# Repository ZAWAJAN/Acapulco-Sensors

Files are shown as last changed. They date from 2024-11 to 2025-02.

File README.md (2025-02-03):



# Acapulco Light Sensors: The Cube and The Camera

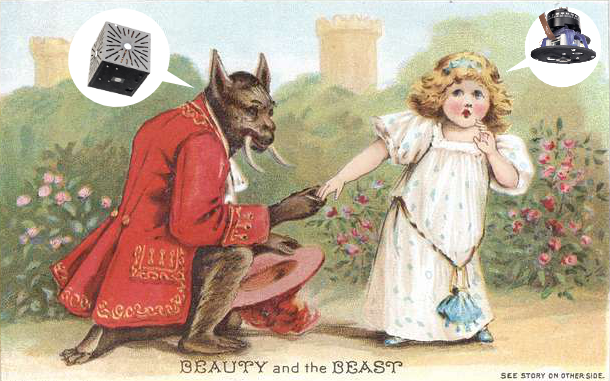
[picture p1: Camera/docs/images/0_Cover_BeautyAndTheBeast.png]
Project Cover - The Beauty and The Beast


## Introduction

The Cube (cubic illuminance sensor) and the Camera (HDR image generation setup) sensors were developed as open hardware devices to support predictive building control as part of the [Acapulco](https://www.thegreenvillage.org/project/acapulco/) research project at the [TU Delft Green village](https://www.thegreenvillage.org/).
The Acapulco project, based in the TU Delft Green Village, The Netherlands, is developing innovative design tools to optimise the sustainability of heating, cooling and lighting systems in commercial buildings. The project focuses on integrating thermal storage, a heat pump with ground and surface water sources, automated outdoor Venetian blinds, daylight-linked lighting controls, and AI-powered predictive controls to enhance energy efficiency, reduce CO2 emissions, and alleviate grid congestion.

## Sensing Devices

The project uses two environmental sensing devices, which are referred to as "sensors" in this documentation. 
Each device is in fact a collection of various sensors and parts.
The two devices are used in combination in the Acapulco project, however, one can be used without the other as they are completely independent in their functions.

In two separate folders you can find all needed instructions to assemble and use the two sensors:
1. [**The Cube**](Cube/)
	- A cubic open-source illuminance sensor designed for environmental monitoring (The Cube).
	- The Cube uses a Raspberry Pi Zero 2W with "Ambient 2 Click" sensors connected via a multiplexer, with additional temperature and humidity sensors, all enclosed in a laser-cut box.
 	- Concept inspired by the work of Xia, L., Pont, S. C., & Heynderickx, I. (2017). *Light diffuseness metric, Part 2: Describing, measuring and visualising the light flow and diffuseness in three-dimensional spaces.* Lighting Research & Technology, 49(4), 428–445. [https://doi.org/10.1177/1477153516631392](https://journals.sagepub.com/doi/10.1177/1477153516631392)
2. [**The Camera**](Camera/)
	 - A camera setup for HDR image generation (The Camera).
	 - The Camera uses a Raspberry Pi 4B, with one additional "Ambient 2 Click" sensor for luminance validation. Attached to the ceiling by 3D-printed parts and standard camera mounting elements.
 	 - Concept inspired by the work of Kruisselbrink, T., Aries, M., & Rosemann, A. (2017). A Practical Device for Measuring the Luminance Distribution. International Journal of Sustainable Lighting, 19(1), 75–90. [https://doi.org/10.26607/ijsl.v19i1.76](https://lightingjournal.org/index.php/path/article/view/76)

## Authors

The sensors design, production, and calibration were performed by:
- [Jan Zawadzki](https://www.linkedin.com/in/jan-zawadzki-a92650213/)
- [Eleonora Brembilla](https://www.tudelft.nl/en/staff/e.brembilla/)
- [Pedro de la Barra Luegmayer](https://www.tudelft.nl/en/staff/p.delabarraluegmayer/)
- [Wouter Beck](https://www.linkedin.com/in/wouterbeck/)

## Acknowledgments 

The development of these sensors was supported by a [Open Hardware Stimulation Fund](https://www.tudelft.nl/open-hardware) from the [TU Delft Open Science Program](https://www.tudelft.nl/en/open-science) and by the RVO MMIP Acapulco project (Grant number TSEGO23017).

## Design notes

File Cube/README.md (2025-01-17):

# Cubic Illuminance Sensor

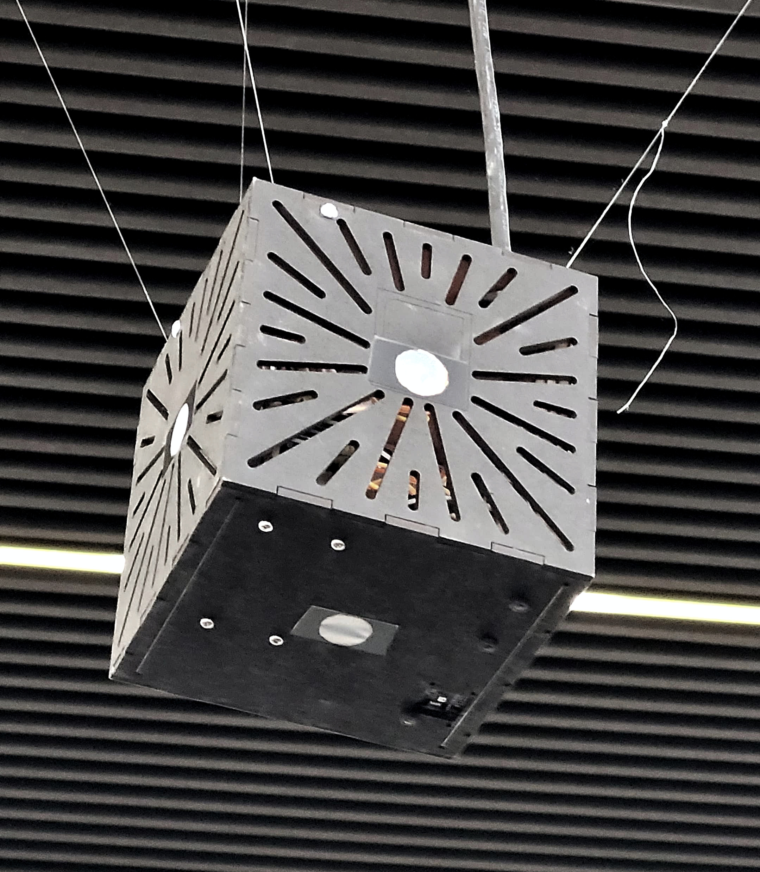
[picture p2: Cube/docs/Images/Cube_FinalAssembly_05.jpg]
Final Cube Image


An open-source cubic illuminance meter designed for environmental monitoring. The device uses a Raspberry Pi Zero with "Ambient 2 Click" sensors connected via a multiplexer, all enclosed in a laser-cut box.

## Features
- Measures ambient light in multiple directions (cubic configuration).
- Customizable design using off-the-shelf components.
- Built with open-source hardware and software principles.

## Table of Contents
1. [Introduction](#introduction)
2. [Bill of Materials (BOM)](#bill-of-materials-bom)
3. [Calibration Setup](#calibration-setup)
4. [Final Setup](#final-setup)
5. [Usage Instructions](#usage-instructions)
6. [Troubleshooting](#troubleshooting)
7. [Contributing](#contributing)
8. [License](#license)

## Introduction
The Cubic Illuminance Sensor is designed to measure light levels from different angles for environmental sensing applications. It is based on a Raspberry Pi Zero 2W and 6 "Ambient 2 Click" sensors.

It is assumed that building such a sensor requires previous knowledge and intent on its purpose. 

If you want to learn more, please refer to [the paper](https://journals.sagepub.com/doi/full/10.1177/1477153516631392) on which our design is based on.

## Bill of Materials (BOM)

The bill of materials can also be found in an excel file [Materials_Bill](Materials_Bill.xlsx). Depending on your location there might be different available providers and prices, but we included the ones we used as a reference.

| Component               | Quantity | Description                           | Example Link                       |
|-------------------------|----------|---------------------------------------|----------------------------|
| Raspberry Pi Zero 2W       | 1        | Small form-factor computer            | [Buy here](https://www.raspberrypi.com/products/raspberry-pi-zero-2-w/)               |
| Raspberry Pi Zero 2W PoE HAT | 1 | Add-on to Raspberry Pi enabling power and data input with just one ethernet cable | [Buy here](https://www.kiwi-electronics.com/en/poe-ethernet-usb-hub-hat-for-rpi-zero-10711)
| Raspberry Pi Zero 2W Heatsink | 1 | Add-on for Raspberry Pi to better dissipate heat generated by the chips | [Buy here](https://www.waveshare.com/zero-heatsink.htm) |
| Ambient 2 Click         | 6        | MikroElektronika Ambient 2 Click Light Sensor mikroBus Click Board | [Buy here](https://nl.rs-online.com/web/p/sensor-development-tools/1360740)               |
| Temperature & Humidity Sensor | 1 | Adafruit AHT20 - Temperature & Humidity Sensor Breakout Board | [Buy here](https://www.kiwi-electronics.com/nl/adafruit-aht20-temperature-humidity-sensor-breakout-board-stemma-qt-qwiic-10419) |
| I2C Multiplexer    | 1        | IC TCA9548A I2C Multiplexer - Adafruit 2717 breakout board for sensor connection | [Buy here](https://www.bitsandparts.nl/IC-TCA9548A-I2C-Multiplexer-Adafruit-2717-breakout-board-p113670)  |
| Ethernet cable | 1 | Ethernet cable for connection, length as needed | [Buy here](https://www.allekabels.nl/utp-kabel/7390/1098220/uutp-kabel-cat-5e.html) |
| Laser-cut MDF case  | 1        | The laser cut elements for custom enclosure assembly. 3mm MDF or other hard sturdy material.   | [CAD Files](#)              |
| Miscellaneous hardware  | -        | Screws, spacers, wiring, etc.         | -                           |

## 1. Calibration Setup

First, you have to calibrate the ==Ambient2Click== sensors. Refer to the [Sensors Calibration Guide](docs/01_Calibration.md) for instructions on how to do it.

## 2. Final Cube Assembly and Setup

After the sensors are calibrated, you can proceed to assemble the final cubic enclosure for all components.

Refer to the [Final Production Guide](docs/02_Final_Production_And_Assembly.md) for instructions.

## 3. Software

Software instructions can be found in the [Running Software](docs/03_Running_Software.md) guide.

## Troubleshooting
- [Common Issues and Solutions](docs/04_Cube_TroubleShooting.md)

## License
This project is licensed under the [MIT License](LICENSE).

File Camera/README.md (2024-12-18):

# Camera HDR sensor

This repository enables you to use commonly available modular components to build an HDR image capture device, 
compliant with Radiance software suite. It comprises of hardware and software to go through calibration process and
mount the camera on the ceiling, or anywhere else, like in the field.

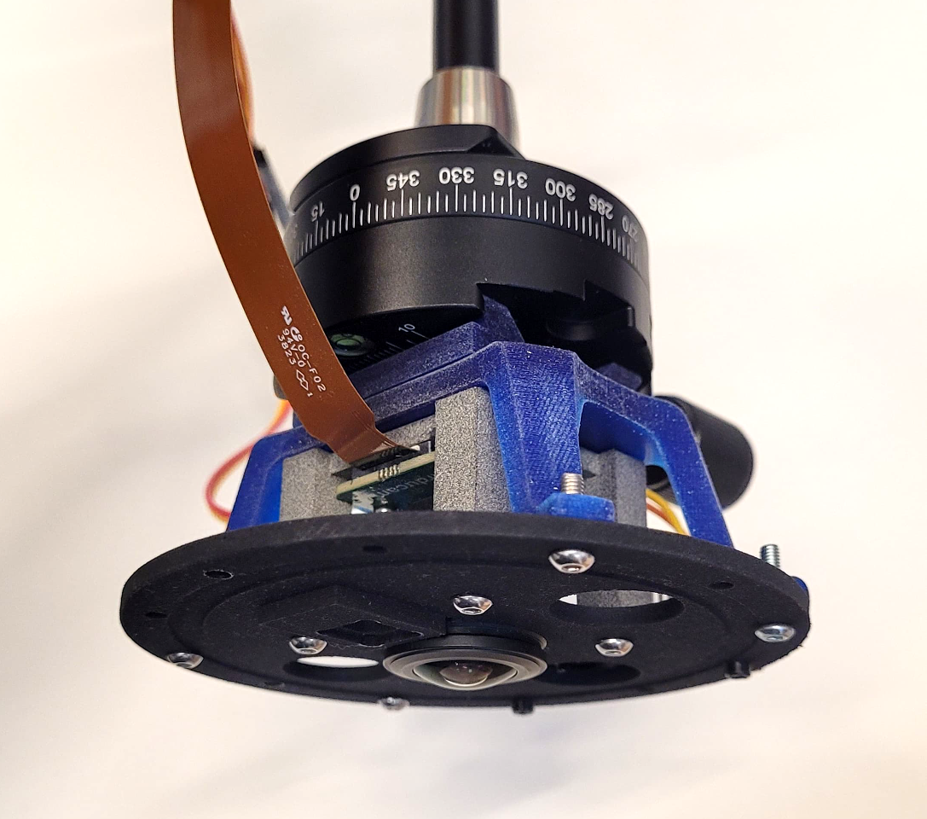
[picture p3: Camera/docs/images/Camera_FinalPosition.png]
Camera attached to the main mounting hold and a regulated arm


## Features
- A low cost way to produce an HDR image remotely, periodically, or in awkward places...
- Takes a series of pictures with varying exposures
- Creates an HDR image using [hdrgen](http://www.anyhere.com/) software
- Via [Radiance](https://www.radiance-online.org/) software, it applies corrections defined during calibration 
process to end up with a proper final HDR image
- Additionally measures luminosity value with an Ambient2Click sensor, for later validation.

## Table of Contents
1. [Introduction](#introduction)
2. [Bill of Materials (BOM)](#bill-of-materials-bom)
3. [Hardware Setup](#hardware-setup)
4. [Software Setup](#software-setup)
5. [HDR Camera Calibration](#hdr-camera-calibration)
6. [Usage Instructions](#usage-instructions)
7. [Troubleshooting](#troubleshooting)
8. [License](#license)

## Introduction

The device uses a Raspberry Pi 4B with an Arducam fisheye camera in order to produce an HDR image. Additionally, 
an illuminance sensor is attached to record a reading that can be helpful later to validate HDR image. The produced 
HDR image can be later used in light studies, glare analysis etc.

## Bill of Materials (BOM)
| Component                  | Quantity | Description                                                                               | Link                       |
|----------------------------|----------|-------------------------------------------------------------------------------------------|----------------------------|
| Raspberry Pi 4B (or other) | 1        | Small form-factor computer. The design also works with other models.                      | [Example](https://www.raspberrypi.com/products/raspberry-pi-4-model-b/)               |
| Raspberry Pi 4 PoE HAT     | 1        | Add-on to Raspberry Pi enabling power and data input with just one ethernet cable         | [Example](https://www.raspberrypi.com/products/poe-plus-hat/)               |
| Raspberry Pi Camera        | 1        | 180° fisheye camera for Raspberry Pi, Arducam Mini imx477 with 180° LN031 fisheye lens    | [Example](https://www.arducam.com/product/arducam-12mp-imx477-mini-high-quality-camera-module-for-raspberry-pi/) |
| Ambient 2 Click sensor     | 1        | MikroElektronika Ambient 2 Click Light Sensor mikroBus Click Board                        | [Example](https://nl.rs-online.com/web/p/sensor-development-tools/1360740)            |
| Ethernet cable             | 1        | Ethernet cable for connection, lenght as needed                                           | [Example](https://www.allekabels.nl/utp-kabel/7390/1098220/uutp-kabel-cat-5e.html)    |
| 3D printed parts           | 1        | High quality, preferably stereolithography polyjet, resin or similar, pla will not cut it  | [CAD Files](src/hardware) |
| Quick Release Rotating Head| 1        | Standard Camera equipment quick release rotating head, preferably with a level meter      | [Example](https://www.kamera-express.nl/b-i-g-qr-60p-panorama-snelkoppeling-60mm)     |
| Laser-cut MDF parts        | 1        | Optional laser cut elements. 3mm MDF or other hard sturdy material.                       | [CAD Files](src/hardware) |
| Miscellaneous hardware     |          | M3 Screws, bolts, and nuts; wires, Rpi camera cable, etc.                                 | Depends on your location  |

## Hardware Setup

0. **3D Printing of parts:**
	- To save time and money, you can produce all the parts at once. You have to do it first anyway.
	- Before doing that, please go through the whole documentation first to know what is needed for what. And if you need to do any adjustments in the CAD files.
	- With the camera ring hold and the lux sensor bracket you have an option, it can be either 3D-printed or laser cut.
	- Parts should be 3D printed in a high quality and sturdy technology, like stereolitography polyjet or resin.
	- You will find all the files in the [hardware folder](src/hardware)
1. **Main Camera Hold:**
	- Camera is being held by a base circular piece in all circumstances.
	- You can refer to the [Main Camera Hold Assembly Guide](docs/00_Camera_Hold_Assembly.md).
1. **Calibration Stand Setup:**
	- You may start with calibrating the camera first, thus better start with assembling the calibration stand.
	- Follow the [Calibration stand assembly guide](docs/01_Camera_Calibration_Assembly.md).
2. **Final Camera Mount:**
	- After the camera is calibrated and all of the correction parameters are defined, you are ready to put your device 
	in place.
	- The final mounting place highly depends on your circumstances, but the use of commonly available camera equipment 
	makes it easy to adjust.
	- Follow the [Final mount assembly guide](docs/02_Camera_Final_Assembly.md).
3. **Wiring Diagram:**
	- In all steps, the wiring stays the same. Refer to the [Wiring Diagram](docs/images/Camera_Wiring_Diagram.png)
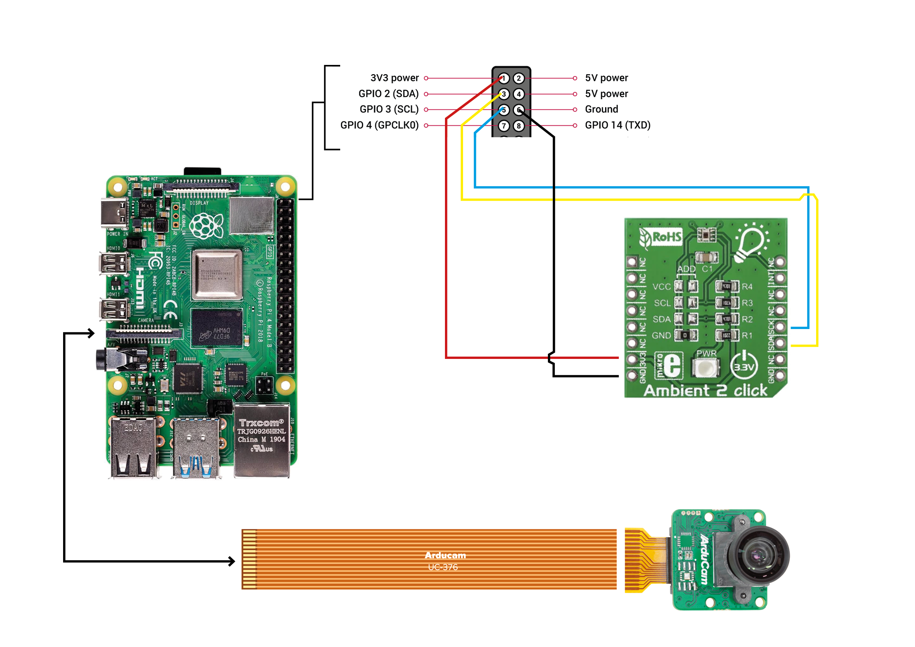
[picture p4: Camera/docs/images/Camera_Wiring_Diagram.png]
Wiring Diagram
	- 

## Software Setup

Before anything, you also have to set up the software needed for everything to run properly.

The software stack that we use is based on the [piHDR](https://github.com/andyrew/piHDR) repository and scripts.

Basic software like [picamera2](https://pypi.org/project/picamera2/) library should be installed automatically 
on your Raspberry Pi, but other things like [Radiance](https://www.radiance-online.org/) is quite tricky to install 
on a Raspberry Pi and looks like rarely anyone is actually doing it. 
But we do!

1. **Installation - Dependencies:**
	- Python - comes by default on the Raspberry Pi Bookworm OS
	- [picamera2](https://github.com/raspberrypi/picamera2) library - should also come by default.
	- [hdrgen](http://www.anyhere.com/) - download the image builder for Raspberry Pi. Or alternatively run:
	 ```bash
	 wget http://www.anyhere.com/gward/pickup/hdrgen_AMDRaspian.tar.gz
	 tar -xf hdrgen_AMDRaspian.tar.gz
	 sudo mv hdrgen /usr/local/bin/.
	 sudo mv hdrcvt /usr/local/bin/.
	 ```
	- imagemagick:
	 ```bash
	 sudo apt-get install imagemagick
	 ```
2. **Enable the Camera Module:**
	- Make sure your camera is connected and works properly.
	- Check the [camera dcumentation](https://www.raspberrypi.com/documentation/computers/camera_software.html)
	- Or alternatively the simple [starters guide](https://projects.raspberrypi.org/en/projects/getting-started-with-picamera/0)
3. **Install and Compile Radiance:**
	- Compiling Radiance on Raspberry Pi can be challenging, especially on newer OS like Bookworm.
	- Refer to the [Radiance Compile Guide](docs/03_Camera_Software_Radiance_Compile.md) to get instructions on 
	how to do it properly, so every app will work.
4. **First run:**
	- Go to the [Usage Instructions](#usage-instructions) and check if things work.
	- Before [Camera Calibration](#hdr-camera-calibration) process, you can only make a basic HDR image, as you don't 
	have the necessary parameters for Radiance correction executables.
## HDR Camera calibration

Each camera module and fisheye lens is different, even if they come from the same manufacturer and the same line.

That's why it's important to apply corrections to the HDR image taken based on those discrepancies. Those corrections 
	are applied with various Radiance apps in the main [bash script](src/code/run_hdrcapture.sh) in consecutive lines after creating 
	an HDR image.

See the [Calibration Guide](docs/04_Camera_Calibration_Guide.md) for detailed instructions.

## Usage Instructions

- In order to only take multiple exposures (images), you can use the python script `exposurebracket.py`.
	 ```bash
	 python3 exposurebracket.py
	 ```
- To run the whole software, simply run `run_hdrcapture.sh`, which will call all necessary scripts and apps.
	 ```bash
	 bash run_hdrcapture.sh
	 ```
- The script will create a new folder in which everything will be stored.
- It also calls the `lux_sensor.py` script providing it with the timestamp. This stores the lux value from the sensor.
- **Note!** In consecutive lines of the `run_hdrcapture.sh`, after the `hdrgen` is run, you can apply various corrections to 
	the HDR via `ra_xyze, pcompos, pfilt` and `pcomb`. Those require parameters and correction `.cal` files specific 
	to your situation, which have to be defined through the calibration process. 
	Again refer to [HDR Camera Calibration](#hdr-camera-calibration)

## License
This project is licensed under the [Solderpad License](http://solderpad.org/licenses/SHL-2.1/).

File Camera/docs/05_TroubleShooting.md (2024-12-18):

# Troubleshooting

## Common Issues
1. **No Sensor Data**
   - Check that the multiplexer is connected properly.
   - Verify that the sensors are powered.

2. **Incorrect Data Readings**
   - Make sure the sensors are not obstructed.
   - Check for proper sensor calibration in the software.

3. **Software Installation Fails**
   - Try running the software with elevated privileges (`sudo`).

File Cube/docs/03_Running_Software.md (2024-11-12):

# Software Guide for Cube Illuminance meter

Now that you have the assembled device ready, you can collect the data from it. There are numerous ways, the data can be collected once, when needed, or it could be a chronological setup, for example using 'cron'.
The code to be used is pretty much the same as the one used during calibration.

Remember to apply the adjustments figured out during the calibration process. That needs to be done by hardcoding it into the provided [python script](src/code/sensor_data_collect_store_csv.py).

# Usage Instructions

You can run the python script directly from the command line, providing a name of the csv file to store the data in, like so:
```bash
python3 sensor_data_collect_store_csv.py "Data_Log_File.csv"
```

Or you could use the [bash script](src/code/run_sensor_collector.sh), which automatically creates a folder named with this days timestamp. In the bash script, at the beginning you can specify the desired directory.
```bash
bash run_sensor_collector.sh
```

The sensor is meant to collect data periodically. 
To set this up, we refer you to [this example guide on cron](https://phoenixnap.com/kb/set-up-cron-job-linux).

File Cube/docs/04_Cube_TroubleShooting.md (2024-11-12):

# Troubleshooting

## Common Issues
1. **No Sensor Data**
	- Check that everything is connected properly.

2. **Incorrect Data Readings**
	- Make sure the sensors are not obstructed.
	- Did you calibrate the sensor properly?

3. **Software Installation Fails**
	- Try running the software with elevated privileges (`sudo`).

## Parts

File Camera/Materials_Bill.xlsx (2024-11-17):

Component | Quantity | Description | Sample Link
Raspberry Pi 4B (or other) | 1 | Small form-factor computer. The design also works with other models. | https://www.raspberrypi.com/products/raspberry-pi-4-model-b/
Raspberry Pi 4 PoE HAT | 1 | Add-on to Raspberry Pi enabling power and data input with just one ethernet cable | https://www.raspberrypi.com/products/poe-plus-hat/
Raspberry Pi Camera | 1 | 180° fisheye camera for Raspberry Pi, Arducam Mini imx477 with 180° LN031 fisheye lens | https://www.arducam.com/product/arducam-mini-high-quality-camera-with-m12-mount-lens-for-raspberry-pi-cm-cm3-cm3-cm4-b0271/
Ambient 2 Click sensor | 1 | MikroElektronika Ambient 2 Click Light Sensor mikroBus Click Board | https://nl.rs-online.com/web/p/sensor-development-tools/1360740
Ethernet cable | 1 | Ethernet cable for connection, lenght as needed | https://www.allekabels.nl/utp-kabel/7390/1098220/uutp-kabel-cat-5e.html
3D printed parts | 1 | High quality, preferably stereolitography polyjet, resin or similar, pla will not cut it | depends on your local availability
Laser-cut MDF parts | 1 | Optional laser cut elements. 3mm MDF or other hard sturdy material. | depends on your local availability
Miscellaneous hardware |  | Screws, bolts, nuts, wiring, Rpi camera cable, etc.

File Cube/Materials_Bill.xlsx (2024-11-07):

Component | Quantity | Description | Sample Link
Raspberry Pi Zero 2W | 1 | Small form-factor computer | https://www.raspberrypi.com/products/raspberry-pi-zero-2-w/
Raspberry Pi Zero 2W PoE HAT | 1 | Add-on to Raspberry Pi enabling power and data input with just one ethernet cable | https://www.kiwi-electronics.com/en/poe-ethernet-usb-hub-hat-for-rpi-zero-10711
Raspberry Pi Zero 2W Heatsink | 1 | Add-on for Raspberry Pi to better dissipate heat generated by the chips | https://www.waveshare.com/zero-heatsink.htm
Ambient 2 Click sensors | 6 | MikroElektronika Ambient 2 Click Light Sensor mikroBus Click Board | https://nl.rs-online.com/web/p/sensor-development-tools/1360740
Temperature & Humidity Sensor | 1 | Adafruit AHT20 - Temperature & Humidity Sensor Breakout Board | https://www.bitsandparts.nl/IC-TCA9548A-I2C-Multiplexer-Adafruit-2717-breakout-board-p113670
I2C Multiplexer | 1 | IC TCA9548A I2C Multiplexer - Adafruit 2717 breakout board | https://www.kiwi-electronics.com/nl/adafruit-aht20-temperature-humidity-sensor-breakout-board-stemma-qt-qwiic-10419
Ethernet cable | 1 | Ethernet cable for connection, lenght as needed | https://www.allekabels.nl/utp-kabel/7390/1098220/uutp-kabel-cat-5e.html
Laser-cut MDF case | 1 | The laser cut elements for cube box assembly. 3mm MDF or other hard sturdy material.
Miscellaneous hardware |  | Screws, spacers, wiring, etc.

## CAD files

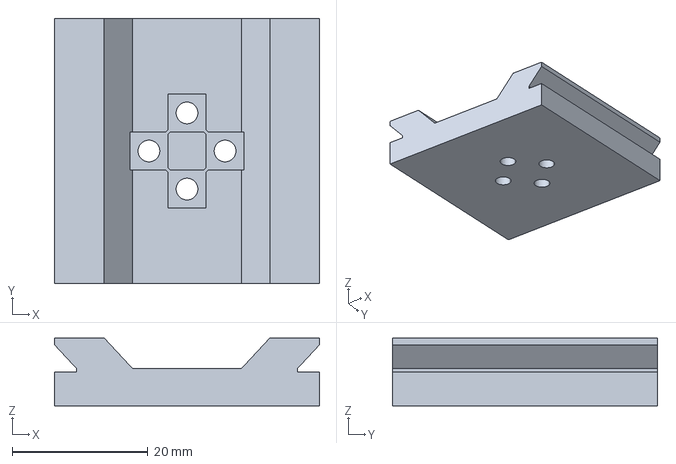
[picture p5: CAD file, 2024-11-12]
Camera/src/hardware/Camera_Mount_Slider.stp
39.0 x 39.0 x 10.0 mm

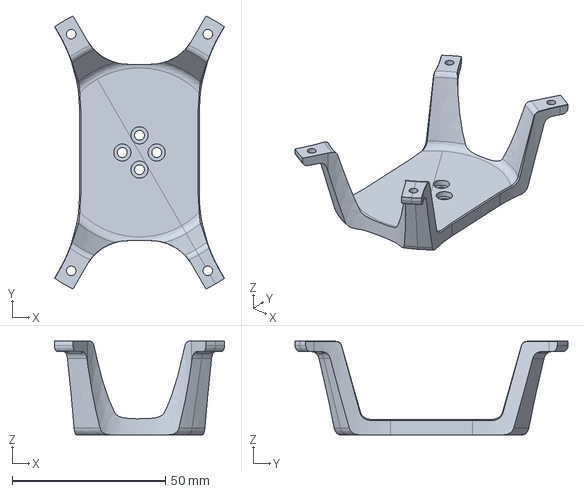
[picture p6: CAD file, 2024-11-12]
Camera/src/hardware/Camera_Mount_Claw.stp
55.4 x 89.0 x 30.5 mm

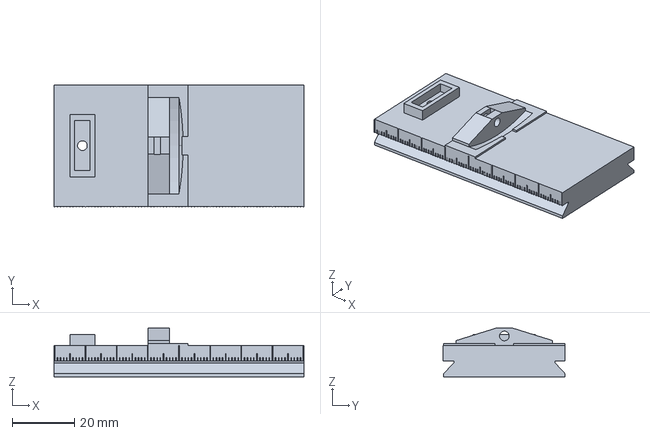
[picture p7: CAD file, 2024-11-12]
Camera/src/hardware/Camera_Calibration_Slider.stp
80.3 x 39.3 x 15.6 mm

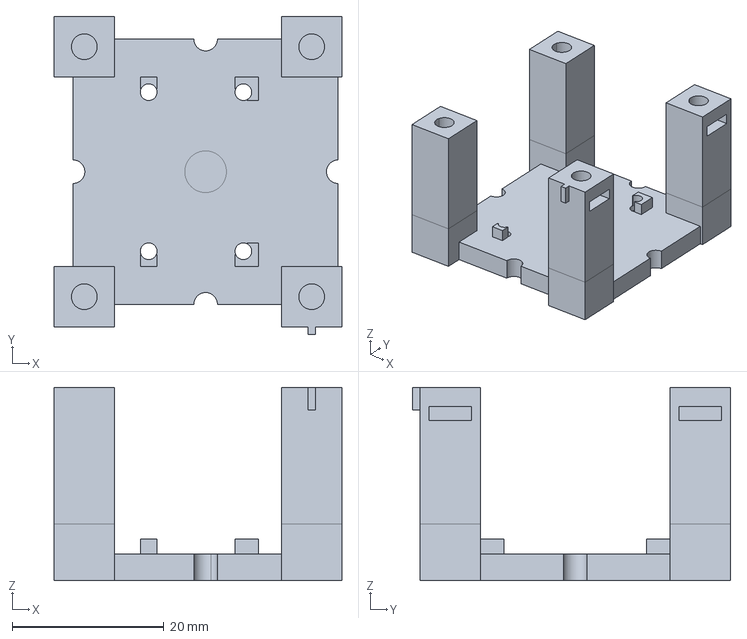
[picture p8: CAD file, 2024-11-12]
Camera/src/hardware/Camera_RingSpacer.stp
38.0 x 42.0 x 25.5 mm

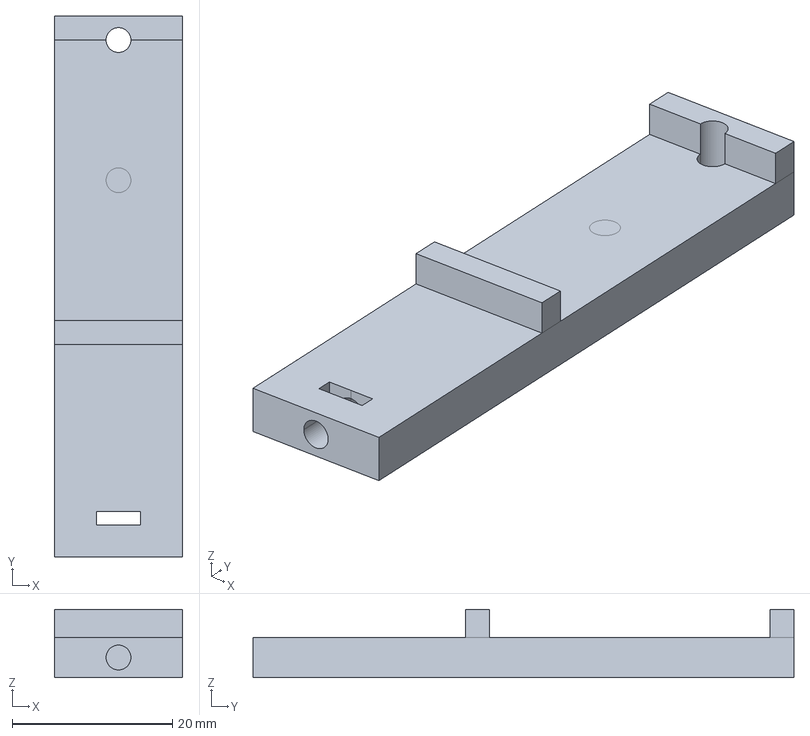
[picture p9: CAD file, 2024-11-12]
Camera/src/hardware/Camera_Calibration_VerticalStand.stp
16.0 x 67.5 x 8.50 mm

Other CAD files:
Camera/src/hardware/Camera_Ring.stp
Cube/src/hardware/Calibration_Bench.dwg
Cube/src/hardware/Cube_Box_Enclosure.dwg
Camera/src/hardware/Camera_RingAndSensorBracket.dwg
Camera/src/hardware/Camera_Calibration_Slider.stl
Camera/src/hardware/Camera_Calibration_VerticalStand.stl
Camera/src/hardware/Camera_Mount_Claw.stl
Camera/src/hardware/Camera_Mount_Slider.stl
Camera/src/hardware/Camera_Ring.stl
Camera/src/hardware/Camera_RingSpacer.stl

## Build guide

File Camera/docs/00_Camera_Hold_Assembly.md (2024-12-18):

# Camera Hold Assembly Guide

In this quick guide you will see instructions on how to assemble the main circular piece that holds the camera. 
That is used further in calibration and final positioning.

**You will need M3 bolts (9-12mm) and M3 square (5.5x5.5mm) nuts for assembly.**

## Assembly Steps

1. **Produce the pieces:**
	- First you need to produce the pieces:
		- Ring - can be 3D printed or laser cut
		- Spacer - Need to be 3D printed
		- Sensor bracket - can be laser cut or 3D printed
	- The Spacer can be 3D printed using [Camera_RingSpacer](../src/hardware/Camera_RingSpacer.stl) file. [STEP](../src/hardware/Camera_RingSpacer.stp) version is also available.
	- The Ring can be 3D printed using [Camera_Ring](../src/hardware/Camera_Ring.stl) file. [STEP](../src/hardware/Camera_Ring.stp) version is also available.
	- The **Ring** can also be laser cut together with the **Sensor Bracket** using the [Camera_RingAndSensorBracket](../src/hardware/Camera_RingAndSensorBracket.dwg) file.
2. **Screw the Camera plate to the Ring Spacer:**
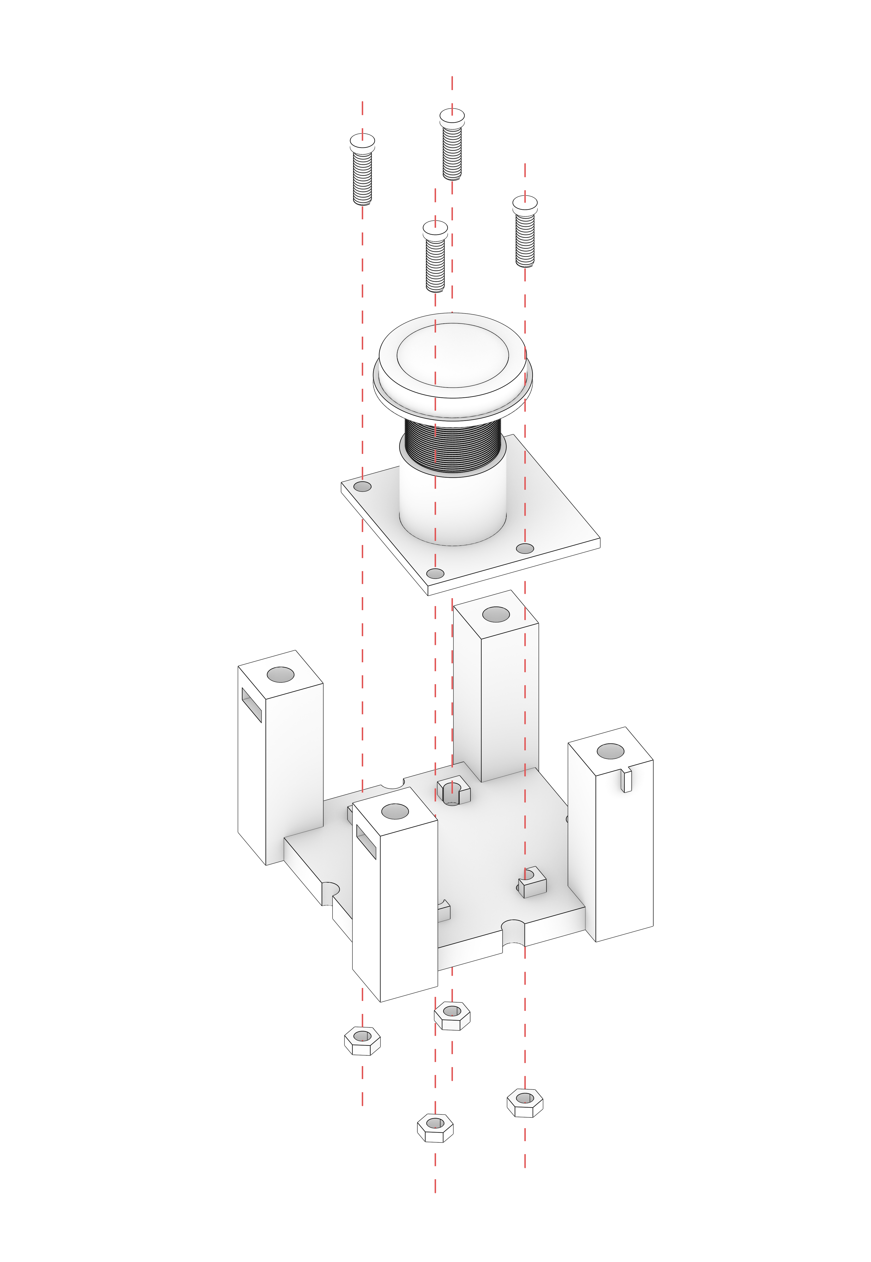
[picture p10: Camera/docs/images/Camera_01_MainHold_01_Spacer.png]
Screw the camera to the spacer
	- 
	- Make sure the camera pcp plate is being screwed in the right position, so that it will be centered with the circular piece and the camera hole.
3. **Screw the Spacer to the Ring:**
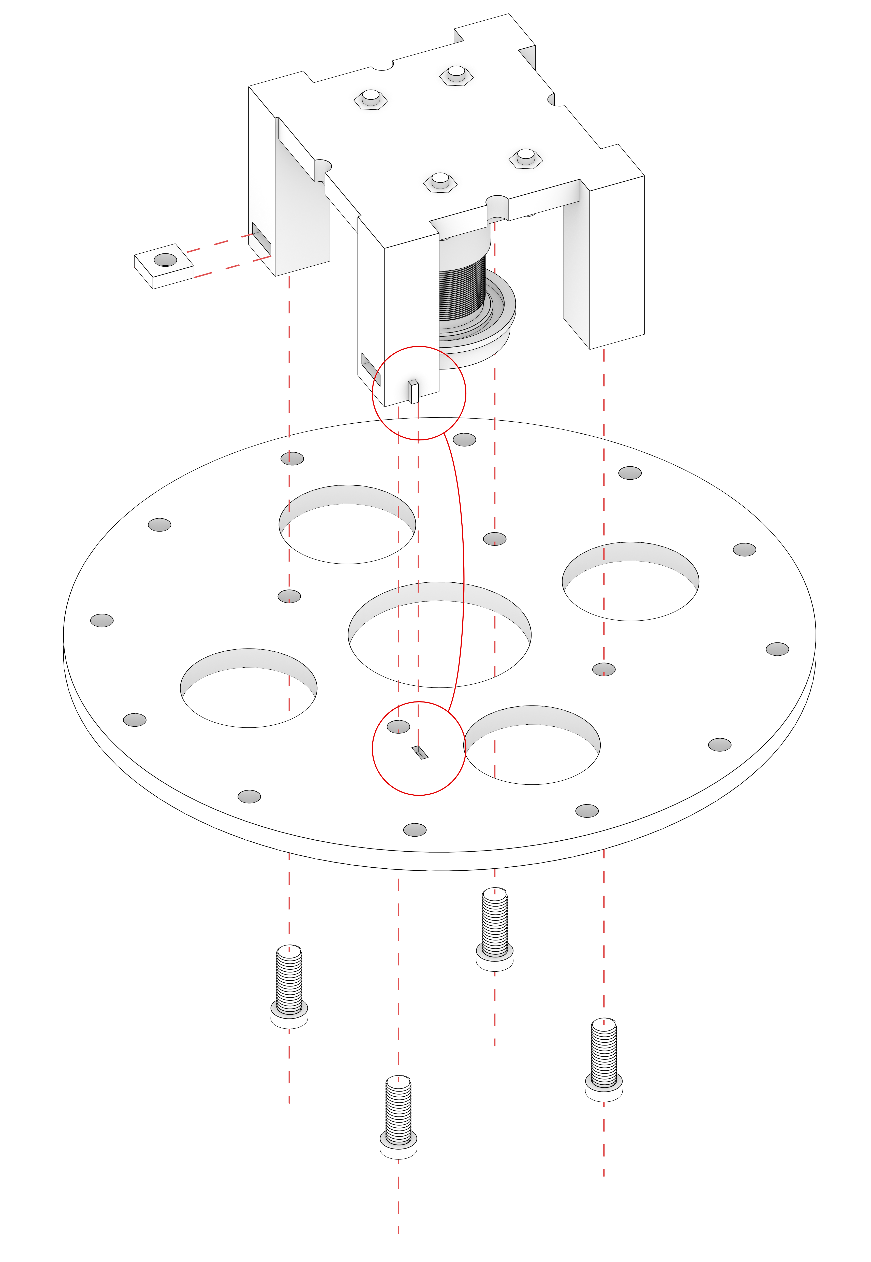
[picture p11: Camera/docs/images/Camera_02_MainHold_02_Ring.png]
Screw the Spacer with Camera to the Ring
	- 
	- Note the small notch on one of the Spacer legs, it tells you how to position it relative to the Ring. This notch should match the small mark on the Ring.
	- Put the square nuts in the special cavities in the Spacer legs.

## End Result

It should look like this after the assembly:

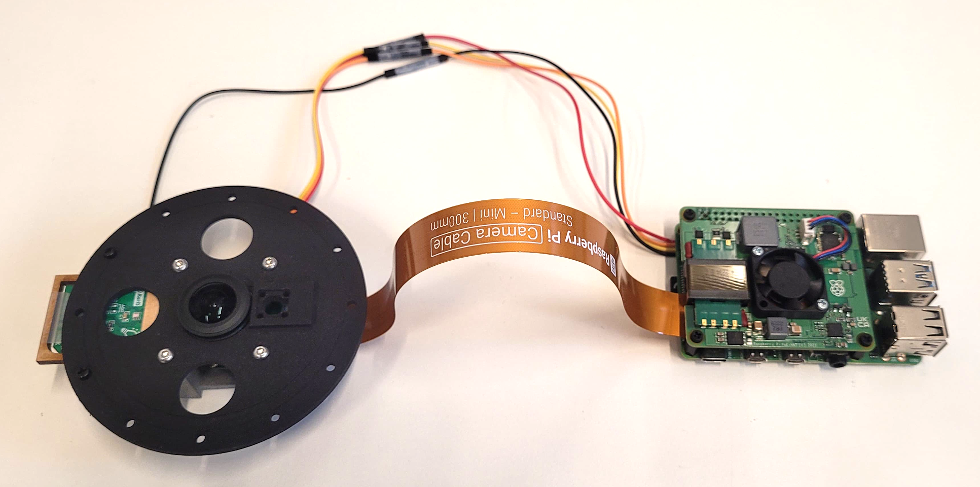
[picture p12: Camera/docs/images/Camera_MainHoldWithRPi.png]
Main Camera Hold Assembled and connected to Raspberry Pi


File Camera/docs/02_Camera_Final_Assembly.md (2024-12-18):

# Camera calibration Stand Assembly Guide

Here you will find instructions on how to assemble the final mounting equipment for the Camera.
You can then use it as you wish depending on where you want the camera to be positioned.

**You will need M3 bolts (9-12mm) and M3 square (5.5x5.5mm) nuts for assembly.**

## Assembly Steps

1. **Produce the pieces:**
	- Here you will need the _Claw_ that holds the Camera ring and the _Slider_ which can be mounted on the Quick Release Head.
	- Both parts need to be 3D printed on high quality:
		- [Camera_Mount_Claw](../src/hardware/Camera_Mount_Claw.stl). - [STEP version](../src/hardware/Camera_Mount_Claw.stp).
		- [Camera_Mount_Slider](../src/hardware/Camera_Mount_Slider.stl). - [STEP version](../src/hardware/Camera_Mount_Slider.stp).
2. **Assemble parts:**
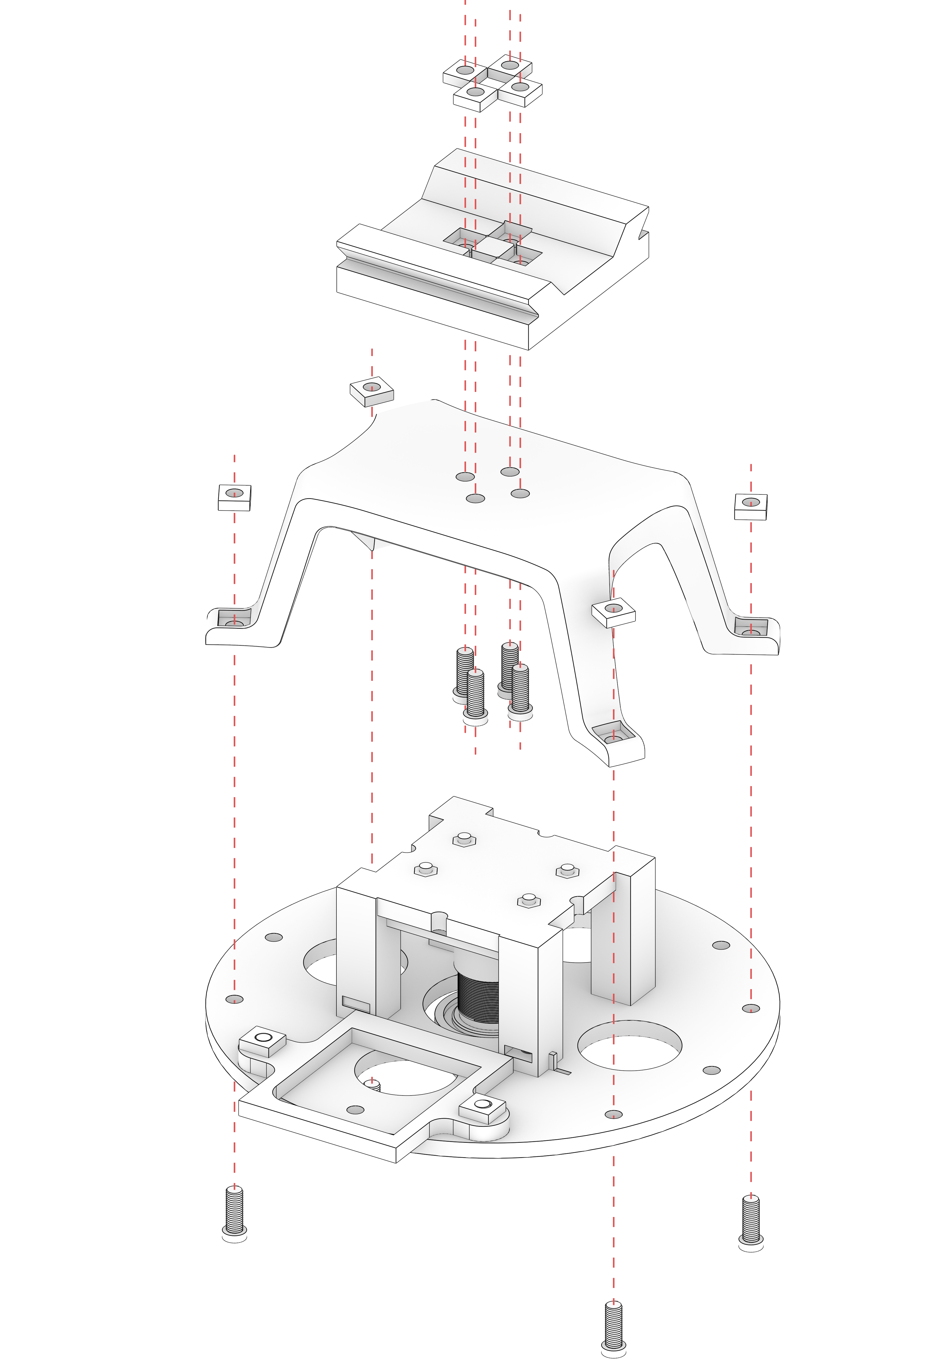
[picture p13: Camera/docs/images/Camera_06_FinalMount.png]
Attach the Claw to the Slider and then the Claw to the Camera Hold
	- .
	- You first need to put bolts into the Claw and attach it to the Slider. It can be attached in different positions thanks to 4 symmetrical holes.
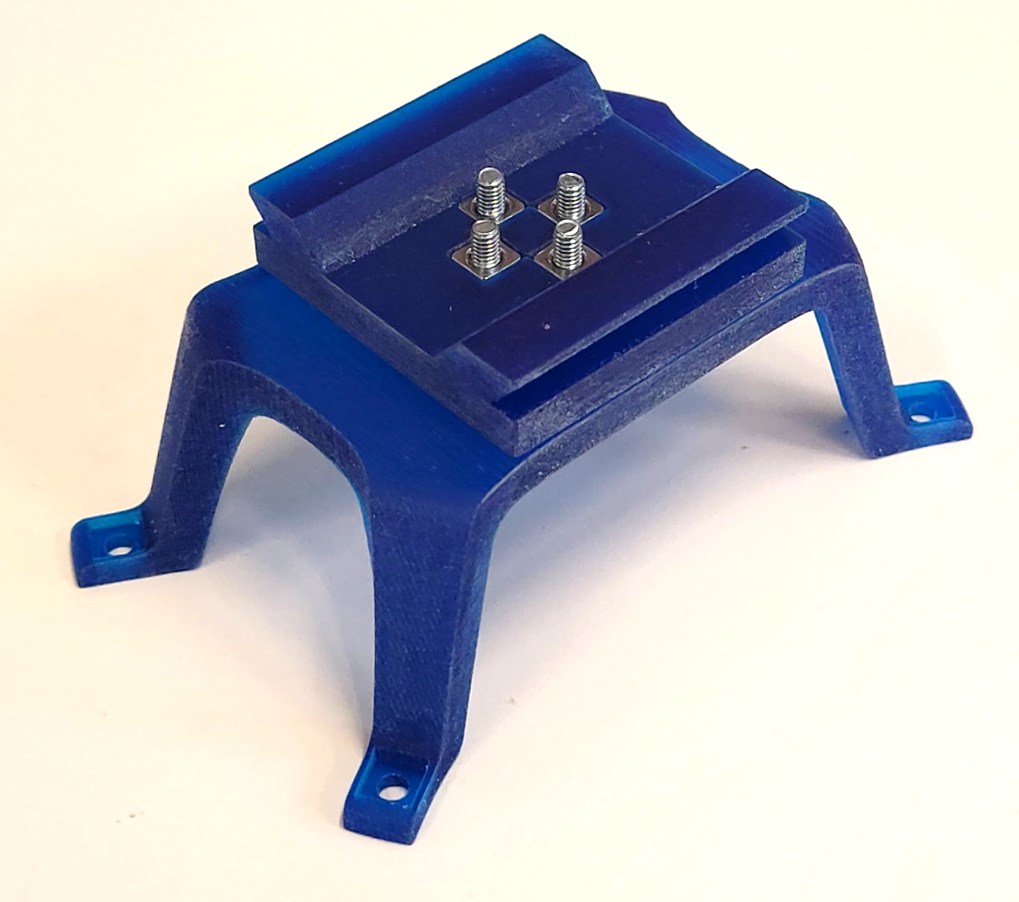
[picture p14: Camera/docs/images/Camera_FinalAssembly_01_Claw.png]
Attach the Claw to the Slider
	- .
	- Then you can attach the Claw to the Ring holding the Camera.
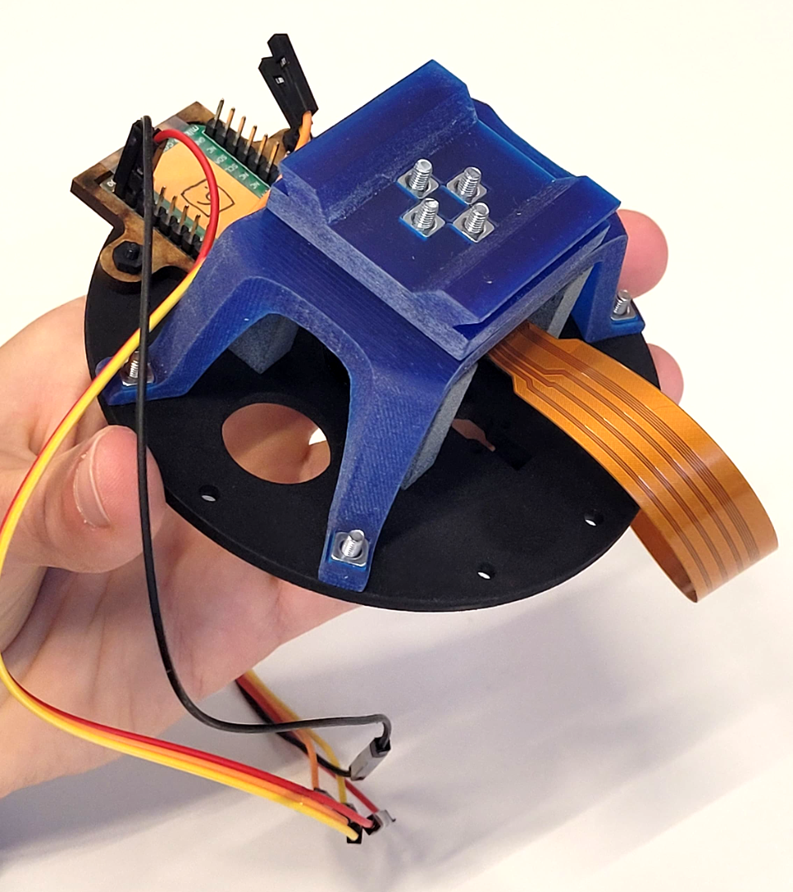
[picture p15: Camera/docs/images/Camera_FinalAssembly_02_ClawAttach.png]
Attach the Claw to the Camera Hold
	- .
	- The Slider can be put in a quick release clamp, which then can be attached to a tripod or regulated arm.

## End Result

It should look like this after the assembly:

Camera attached to the main mounting hold and a regulated arm

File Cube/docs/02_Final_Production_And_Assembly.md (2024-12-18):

# Cubic Enclosure Assembly Guide

After sensors calibration, you can assemble the final cubic device. This guide will help you assemble the laser-cut enclosure for the Cubic Illuminance Meter.

## Required Tools
- Laser-cut mdf panels
- Milky white tape (to cover sensor holes)
- Masking tape (easily removable)
- Black matte spray paint
- Glue (normal hobby wood glue will suffice)
- Hot glue
- Screwdriver with hexagonal bit
- Strong string

## Assembly Steps
1. **Prepare the Cube Panels:**
	- Laser cut the elements of the cube using the provided [CAD file](../src/hardware/Cube_Box_Enclosure.dwg).
	- Identify each panel after cutting - number them according to which sensor will placed on each one (for easier reference).
	- **Note!** Try assembling the box in your hands, make sure everything fits together.

2. **Spray painting:**
	- Put the milky tape on the outsides of each panel to cover the sensor holes. As explained earlier, this tape enables the light to be more scattered and even.
	- From the masking paper tape - cut circles the size of holes - and put them on the tape covering the holes. This will prevent the black paint from staining the sensor openings.
	- You can also cover the holes on the inward side - to make sure nothing contaminates the tape form the other side.
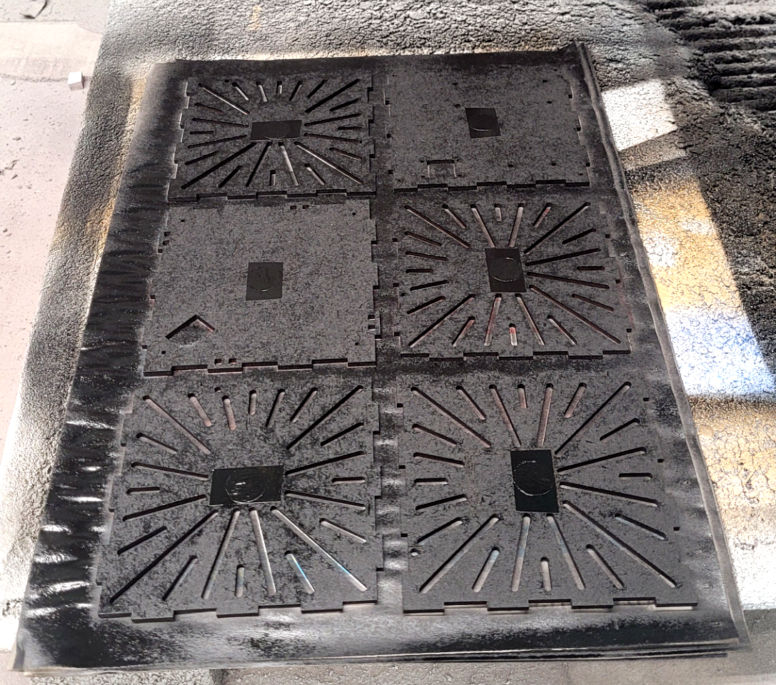
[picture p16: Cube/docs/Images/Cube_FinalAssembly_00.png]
Spray paint panels - don't forget the masking tape
	- 
	- Apply black matte spray paint on the outsides of the panels.
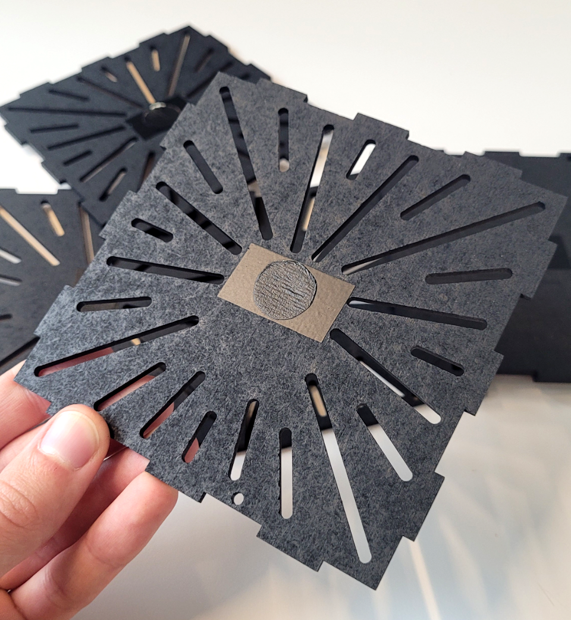
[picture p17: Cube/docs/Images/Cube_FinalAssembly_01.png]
Finished panel with masking tape on
	- 

3. **Panel Preparation:**
	- Remove the masking tape from the inside of each panel.
	- Glue the sensor brackets to each panel according to the engraved outline.
	- Glue the little bolt holders to the top panel. You can see small square holes for that purpose. You can already glue the bolt nuts to the insides of the bold holder elements. 

4. **Attach the Sensors:**
	- Secure each _"Ambient 2 Click"_ sensor inside the enclosure bracket. The sensor itself should be in the middle of the hole.
	- Each sensor should be numbered, as during calibration, so now you can put the sensors in the same numbered panel.
	- Tape the sensors so they are secured properly.

5. **Install the Raspberry Pi, Multiplexer, and the Temp Meter:**
	- Mount the Raspberry Pi on the PoE HAT (if you haven't done so already). Mount the heatsink on top of the Raspberry Pi. Use the screws and spacers provided with the extensions.
	- Mount the RPi brick in the designated spot on the bottom panel. Use the bolts and spacers to secure it in place.
	- Do the same with the TCA9548A Multiplexer and the Temperature and Humidity Sensor. The temperature sensor should face the outside through the hole that is there for this purpose.
	- Ensure connections are secure.

6. **Final Assembly:**
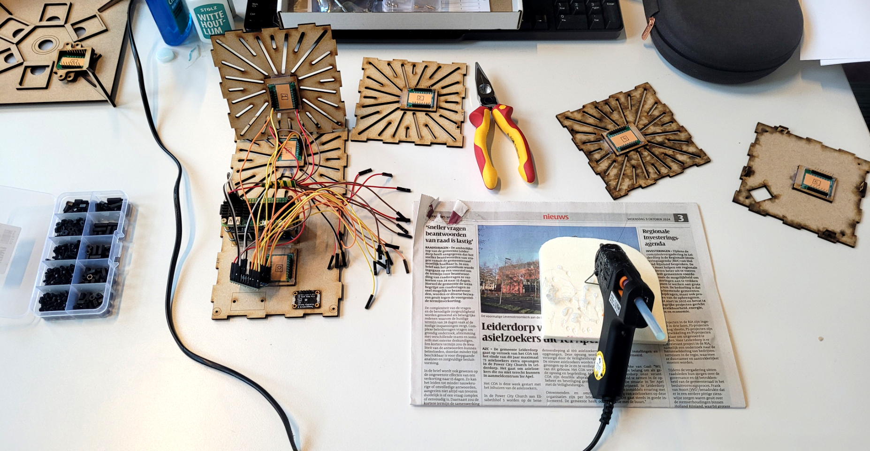
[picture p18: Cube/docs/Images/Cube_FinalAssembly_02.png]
Cube assembly start
	- 
	- We recommend starting with wiring the bottom panel elements with 3 side panels. This way you leave one of the side panels and the top panel for later, making it easier to connect things inside.
	- Refer to the same [Wiring Diagram](Images/Wiring_Diagram.png) as during the calibration process.
	- Use the hot glue to secure wires in place, so they don't eject spontaneously after the case is closed.
	- Join the panels together using glue. It can be a bit of a spaghetti inside, so be patient and careful.
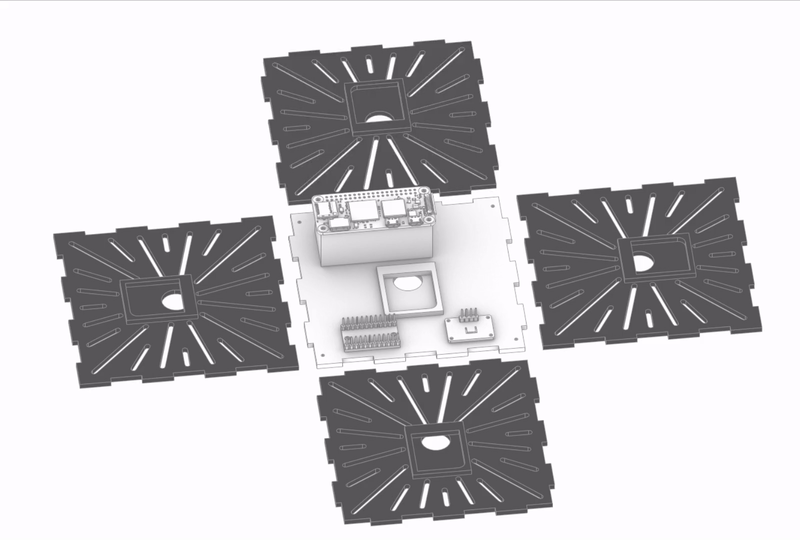
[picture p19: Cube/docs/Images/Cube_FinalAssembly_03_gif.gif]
Cube Assembly Animation
	- 
	- **Note!** Remember about the Ethernet cable for the Raspberry Pi. Best to plug it in before the 4th and top walls are in place. The ethernet cable goes though the hole in the top panel.
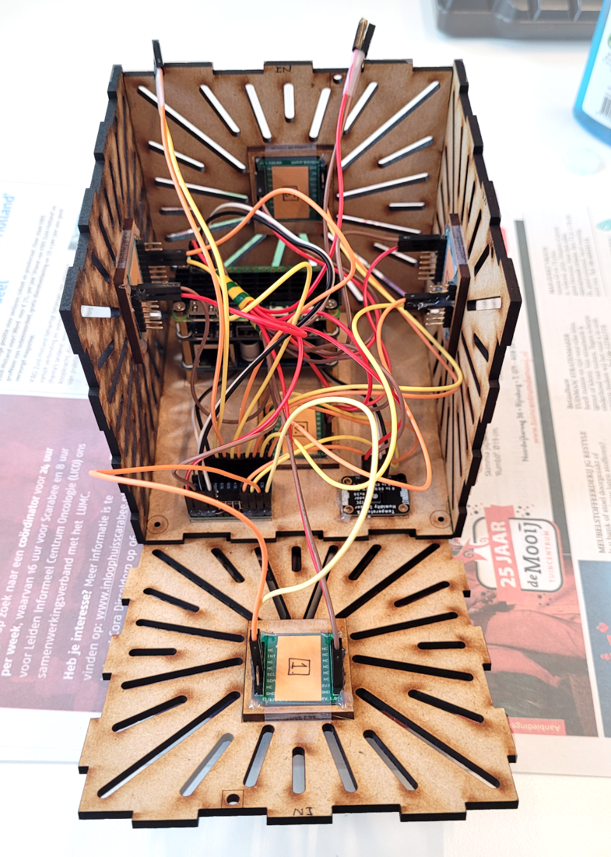
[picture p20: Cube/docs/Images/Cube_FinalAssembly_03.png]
Cube assembly finish
	- 
	- At this point you can also wire through the strings that will hold the cube in the air. Use the little holes in the corners of the bottom and top panels. Refer to the [String Mount Diagram](Images/Cube_FinalAssembly_05.png).
	- Put the top panel in place. Secure it with bolts through the 4 holes in the side panels. The bolts should go though the holes, bolt holders and bolt nuts glued to the bolt holders. This way it's secured nicely and can be easily dismantled in case a need for a quick repair arises.
	- Tighten all connections and make sure if you did not forget about anything.
7. **Final Placement:**
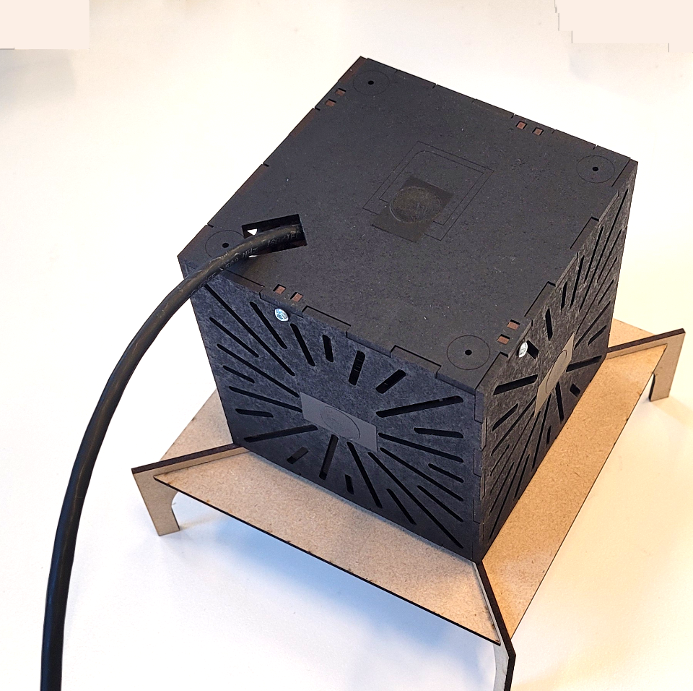
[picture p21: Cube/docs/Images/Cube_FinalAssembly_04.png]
Finished Cube ready for placement
	- 
	- Now the software should be tested to see whether you get correct data and if some of the connections did not get loose.
	- Remove the masking tape from the holes.
	- Hang the cube attaching it to the ceiling or something else. That highly depends on your setting.

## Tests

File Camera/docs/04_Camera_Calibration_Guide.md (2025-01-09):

# HDR Camera Calibration Guide

To end up with a standardized and useful HDR image, various adjustments have to be applied after the multiple exposures are taken and the base HDR image is produced with hdrgen.

This whole process is described in the [Tutorial: Luminance Maps for Daylighting Studies from High Dynamic Range Photography](https://infoscience.epfl.ch/bitstreams/5de7b455-0f0b-4cba-be41-0478e5abb181/download) in detail. 
We will not cover it extensively here, so please refer to beforementioned paper.

## Calibration Steps

Adapted from [Clotilde Pierson. Coralie Cauwerts, Magali Bodart, Jan Wienold, 2020](https://www.researchgate.net/publication/338386406_Tutorial_Luminance_Maps_for_Daylighting_Studies_from_High_Dynamic_Range_Photography).

1. Response function
	- This is being done automatically by `hdrgen` while merging the multiple exposures into an HDR image. An `.rsp` file is created.
	- Best practice is to generate couple of different response function correction files while making an HDR image in the final scene, testing different stable light conditions.
	- The one chosen correction file is then reused for every new HDR generation by providing it to the `hdrgen` command.
	- More explanation can be found in the main `bash` [file](../src/code/run_hdrcapture.sh) generating the HDR image.
2. Cropping and resizing the HDR image
	- This crops the image to square encompassing a circle of your lens fisheye view.
	- You have to know dimensions of your Image and pixel coordinates. This can be done in any image editing software like Gimp, Affinity Photo or Photoshop.
3. Projection Adjustment:
	- You need to figure out the projection of you fisheye camera and apply a specific correction in a .cal file
	- Refer to [A method for estimating fisheye lens’ field-of view angle and projection for HDR luminance capture](https://pure.tudelft.nl/ws/portalfiles/portal/57456665/x046_PO061.pdf) for instructions.
4. Vignetting Correction - Determination of Vignetting Curves:
	- You have to determine the rate at which the HDR image is getting darker towards the edges of the fisheye circular field of view.
	- You can find instructions on page 13 of the paper.
	- Also refer to [this blog post](https://discourse.radiance-online.org/t/help-with-creating-a-vignetting-cal-file/5745), and [this one](https://discourse.radiance-online.org/t/vignetting-correction-calibration-file/5962).

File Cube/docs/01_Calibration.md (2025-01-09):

# Cube Device Sensors calibration

For accurate results, before you assemble the final cubic device it is best to calibrate each of the _Ambient2Click_ lux sensors against a research-grade luxmeter.

Here we assume you will have to borrow a professional illuminance meter for the calibration process, like the [Konica Minolta T-10MA](https://www.konicaminolta.eu/eu-en/hardware/measuring-instruments/light-and-display-measurement/illuminance-meters/t-10a-t-10ma) that we used.

The calibration process needs a stable environment and light source. We performed the calibration in two environmental settings:
1. electric light in a dark room
2. room with a single window during a stable overcast day

During calibration, all sensors should be as close as possible to the reference luxmeter. For this purpose, a custom laser cut calibration bench can be fabricated using the provided [CAD files](../src/hardware/Calibration_Bench.dwg) - see explanation below.

## Hardware Assembly - Calibration Setup

1. **Calibration Bench:**
	- You can find the CAD file for the Calibration Bench [here](../src/hardware/Calibration_Bench.dwg)
	- Laser cut and assemble the calibration bench. Refer to the [Instructions](Images/Cube_Calibration_00_Bench_Assembly_Diagram.png) provided. Use glue to stick the sensor brackets to the main board with holes.
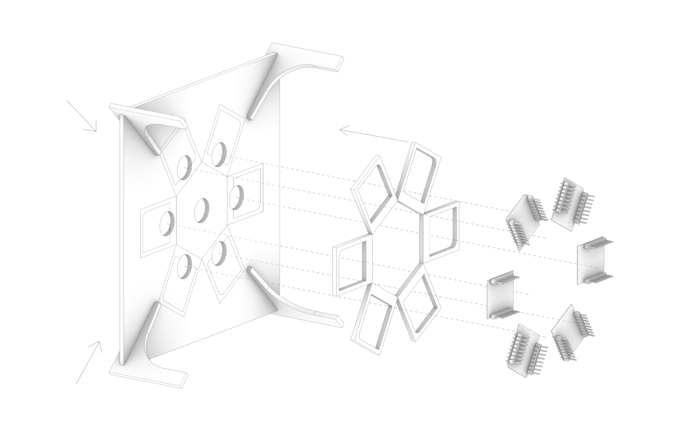
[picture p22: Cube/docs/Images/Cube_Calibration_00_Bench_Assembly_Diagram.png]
Calibration Bench Assembly Diagram
	- 
	- Place the sensors in the slots on the back of the bench. Number them so you know which one is which. Use tape to keep them in place.
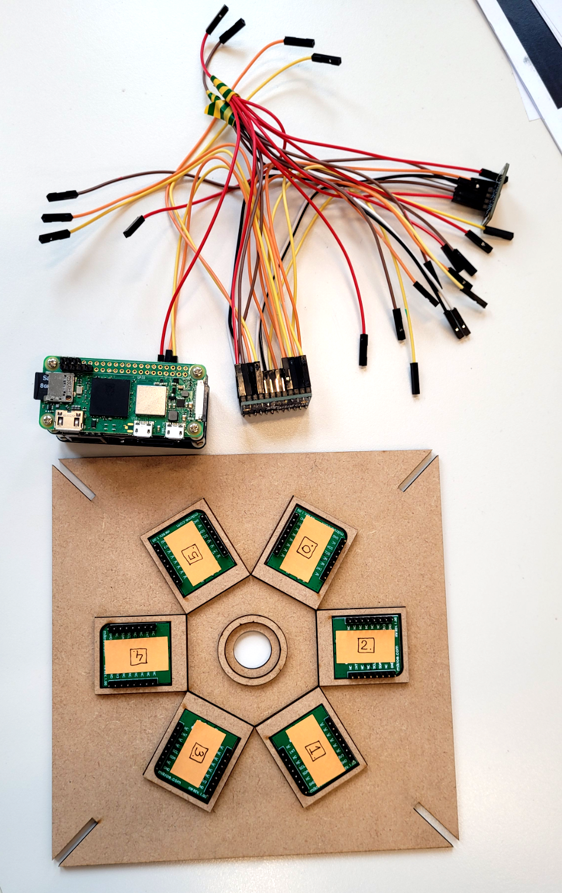
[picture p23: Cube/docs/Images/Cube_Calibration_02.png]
Put sensors in place
	- 
	- There is one additional hole in the centre of the bench face - it can be used either to place the reference meter (which we did for our purposes), or an additional sensor to be calibrated.
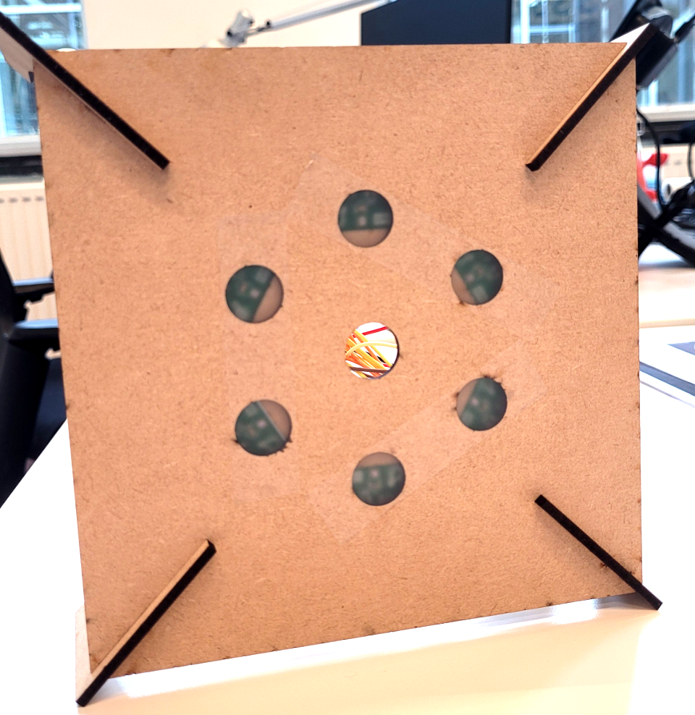
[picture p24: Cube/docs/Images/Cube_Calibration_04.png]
Put tape on the holes
	- 
	- Use a matte scotch tape to cover the holes through which the sensors look outwards. This is supposed to improve the cosine response of the sensors, although the case geometry is not engineered for this as in professional luxmeters.
2. **Wire:**
   - Connect the "Ambient 2 Click" sensors to the TCA9548A multiplexer
   - The humidity and temperature sensor is not needed in this step, but you can also connect it to the multiplexer
   - Wire the multiplexer to the Raspberry Pi Zero
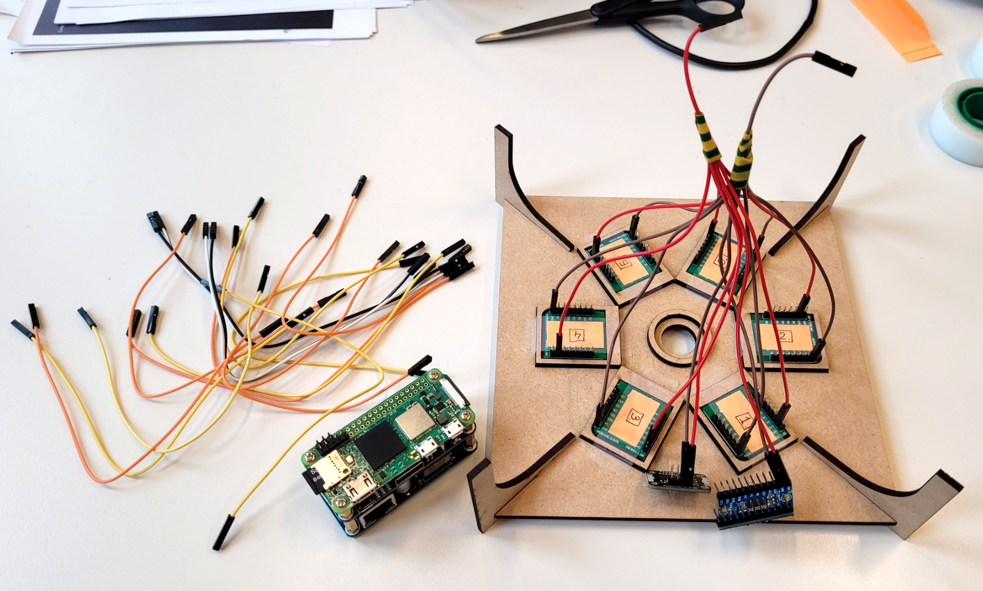
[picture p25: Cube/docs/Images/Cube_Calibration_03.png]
Wire components together
   - 
   - Follow the [Wiring Diagram](Images/Wiring_Diagram.png)
   - Wiring Diagram
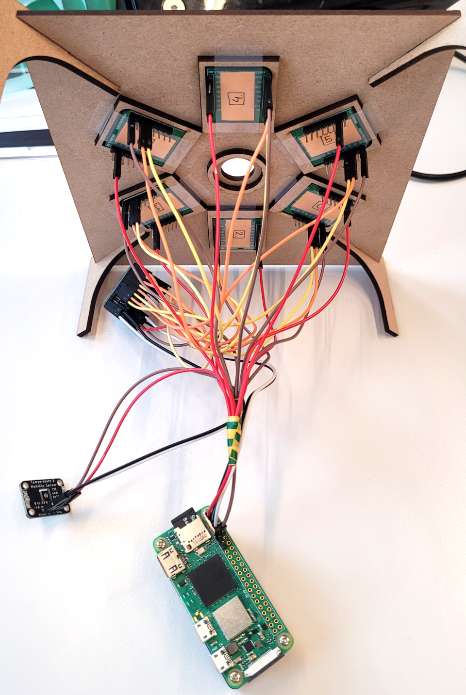
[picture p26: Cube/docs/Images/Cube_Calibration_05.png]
Final wired calibration bench
   - 
3. **Desk Setup:**
	- Print an angle measuring sheet. This will help you rotate the bench evenly each measurement step
	- The bench centre should also be in the center of rotation

## Software

1. **Installation:**
   - The code is tested and running on a Raspberry Pi Bookworm OS
   - Before anything else, update your Raspberry Pi system and libraries:
     ```bash
     sudo apt-get update
	 sudo apt-get upgrade
     ```
   - All the required python libraries (smbus, time, csv, argparse) should be installed by default on a Raspberry Pi system.
2. **Running the Software:**
   - Execute the python script [sensor_data_collect_store_csv.py](../src/code/sensor_data_collect_store_csv.py) to capture readings directly to a .csv file in the same folder:
     ```bash
     # Run the Python script, passing the CSV file as an argument
	 python3 sensor_data_collect_store_csv.py "CSV_FILE.csv"
     ```
   - Or use the bash script [run_sensor_collector.sh](../src/code/run_sensor_collector.sh), in which you have to specify the destination folder. The script will automatically create a new .csv file named with the current day:
     ```bash
     sudo bash run_sensor_collector.sh
     ```
   - Check if the readings make sense and if everything is stored properly. Refer to [Cube_Troubleshooting](04_Cube_TroubleShooting.md) in case problems arise.
3. **Proceed to Calibration**

## Calibration Steps

1. **Table Setup**
	- Place the light source and the center of the calibration bench on the same height
	- The distance from the light source to the calibration bench should be roughly 5 times the diameter of the light source
	- Place the calibration bench on the angular measure centre, so it rotates on the axis of the center (the centre sensor in the middle of the bench)
	- Start with the bench facing the light source.
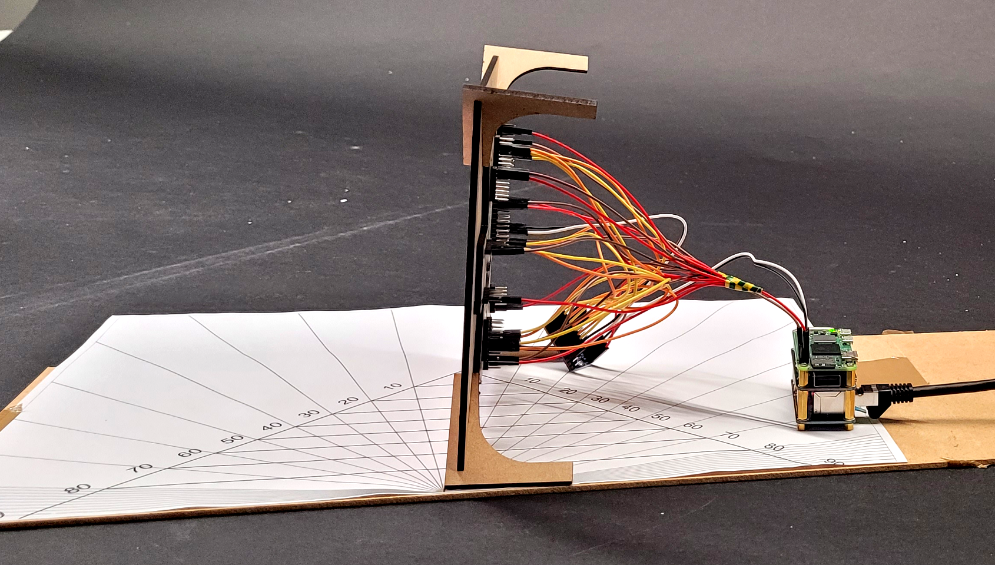
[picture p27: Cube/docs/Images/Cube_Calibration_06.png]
Calibration bench ready for calibration
	- 
	- Make sure there are no other visible light sources to minimise the measurement interference.
2. **Take a measurement**
 	- Run the [run_sensor_collector.sh](../src/code/run_sensor_collector.sh) bash script, which will create the csv file with measurements. Each time you run the script, new measurements will be added as next rows.
	```bash
	sudo bash run_sensor_collector.sh
	```
 	- As you can see, the measurements are also displayed in the command line, make sure they look correct. For example, it may happen that the first measurement is 0. Then just take another one and it should work properly.
	- Next, take measurements with the reference meter. To be thorough, you should take a measurement for each of the sensors, keeping the measuring piece as close to the sensor, basically covering it. Store the measurements in an excel file together.
	- The basic idea is that you should have stable measurements for each of the sensors - one directly from the sensor, and one from the reference sensor.
4. **Repeat with other angles and environment setting:**
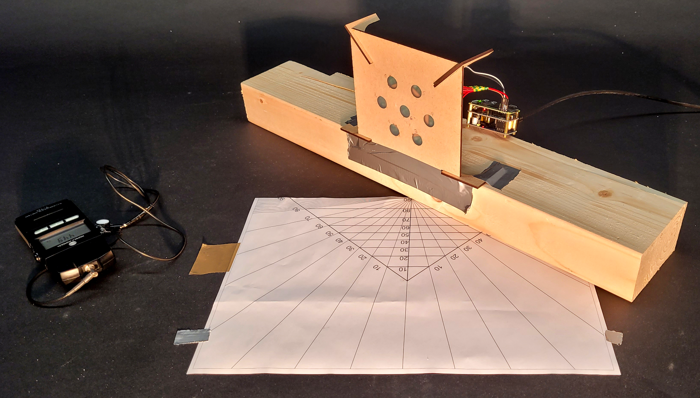
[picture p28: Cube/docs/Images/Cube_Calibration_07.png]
Calibration setup rotated
	- 
	- Rotate the calibration bench by 15°.
	- Take and store measurements until you reach the 90° mark.
	- repeat the whole process in a daylight room setting.
5. **Example Calibration csv structure:**

| Angle | Sensor Number (ID) | Sensor Reading |
| ----- | ------------------ | -------------- |
| 0     | Sensor 0           | 500            |
| 0     | Sensor 1           | 532            |
| 0     | Sensor 2           | 498            |
| 0     | Sensor ....        | ---            |
| 0     | Sensor Reference 0 | 512            |
| 0     | Sensor Reference 1 | 543            |

5. **Compare and adjust**
	- Compare readings from sensors with the reference sensor on a graph and calculate the mean bias error across all angles, for each sensor.
	- Apply the adjustments to each sensor to minimize any bias error and hardcode them in the code of the measuring script.
6. **Apply calibration in the code:**
	- Go to the [sensor reading script](../src/code/sensor_data_collect_store_csv.py)
	- Find the `read_lux()` function definition and navigate to the end of it.
	- Here, before the final `lux_corrected` value is returned, you should apply the required modification for correction, based on the calibration performed.

## End

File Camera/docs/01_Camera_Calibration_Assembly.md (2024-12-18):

# Camera calibration Stand Assembly Guide

In this guide you will see instructions on how to assemble the Sliding Stand to be used for camera calibration. 
It will be used only during the Calibration process to determine the true parallax point and to keep the Camera still in various positions.

**You will need M3 bolts (9-12mm) and M3 square (5.5x5.5mm) nuts for assembly.**

## Assembly Steps

1. **Produce the pieces:**
	- For Calibration you will need the _Sliding Base_ and the _Vertical Support Stand_ to keep the Camera in place.
	- Both pieces need to be 3D printed:
		- [Camera_Calibration_Slider](..src/hardware/Camera_Calibration_Slider.stl) - [STEP version](..src/hardware/Camera_Calibration_Slider.stp)
		- [Camera_Calibration_VerticalStand](..src/hardware/Camera_Calibration_VerticalStand.stl) - [STEP version](..src/hardware/Camera_Calibration_VerticalStand.stp)
	- You will also need the _Sensor Bracket_ - it can be laser cut using the [Camera_RingAndSensorBracket.dwg](..src/hardware/Camera_RingAndSensorBracket.dwg) file.
2. **Screw the Vertical Stand:**
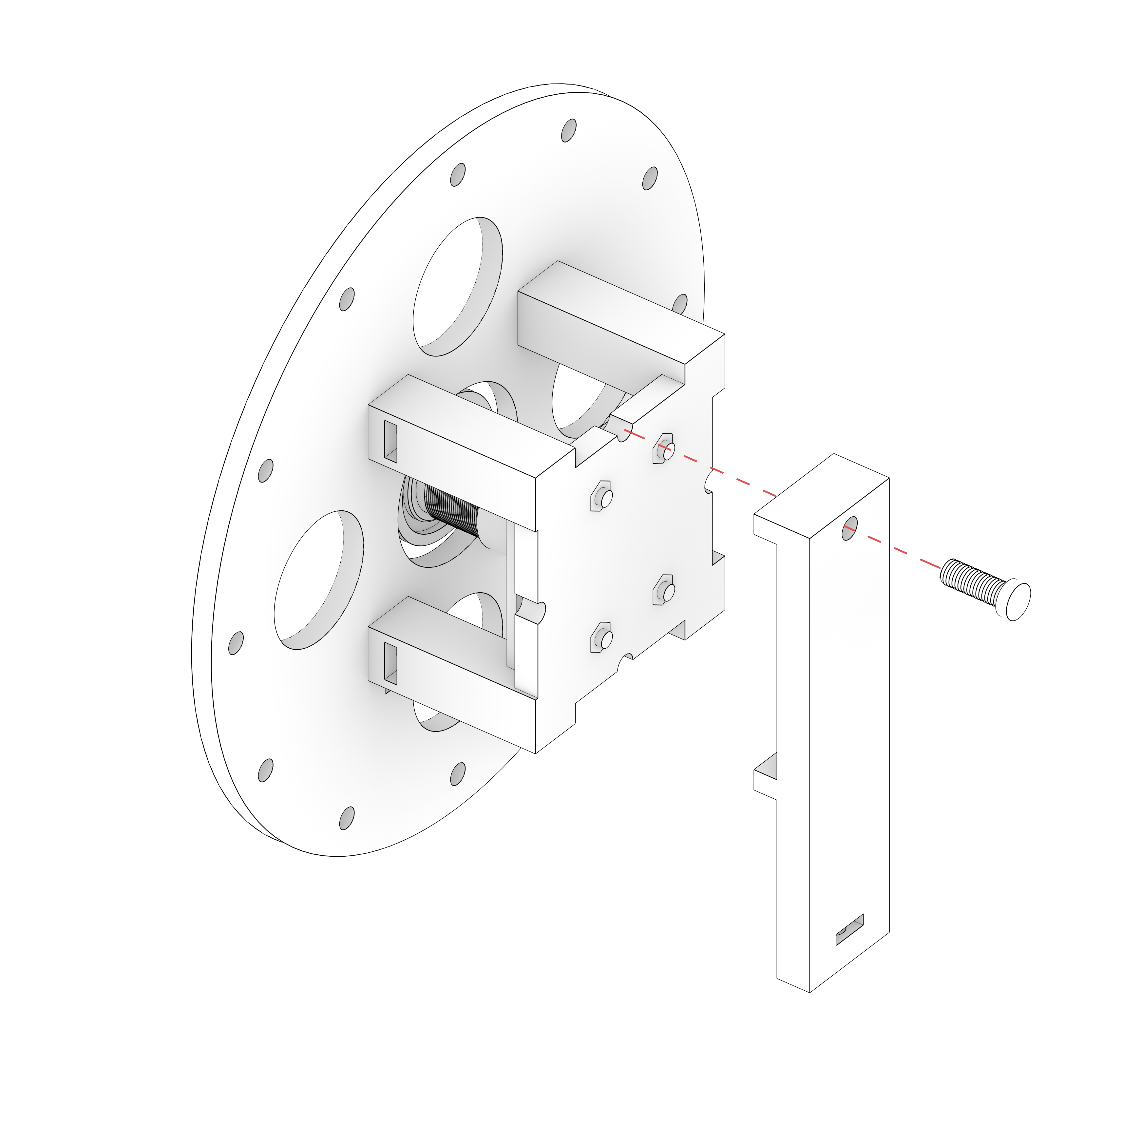
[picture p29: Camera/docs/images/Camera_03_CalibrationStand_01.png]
Screw the Vertical Stand to the Camera Mount back
	- 
	- You can position the Ring how you need.
3. **Screw everything to the Slider:**
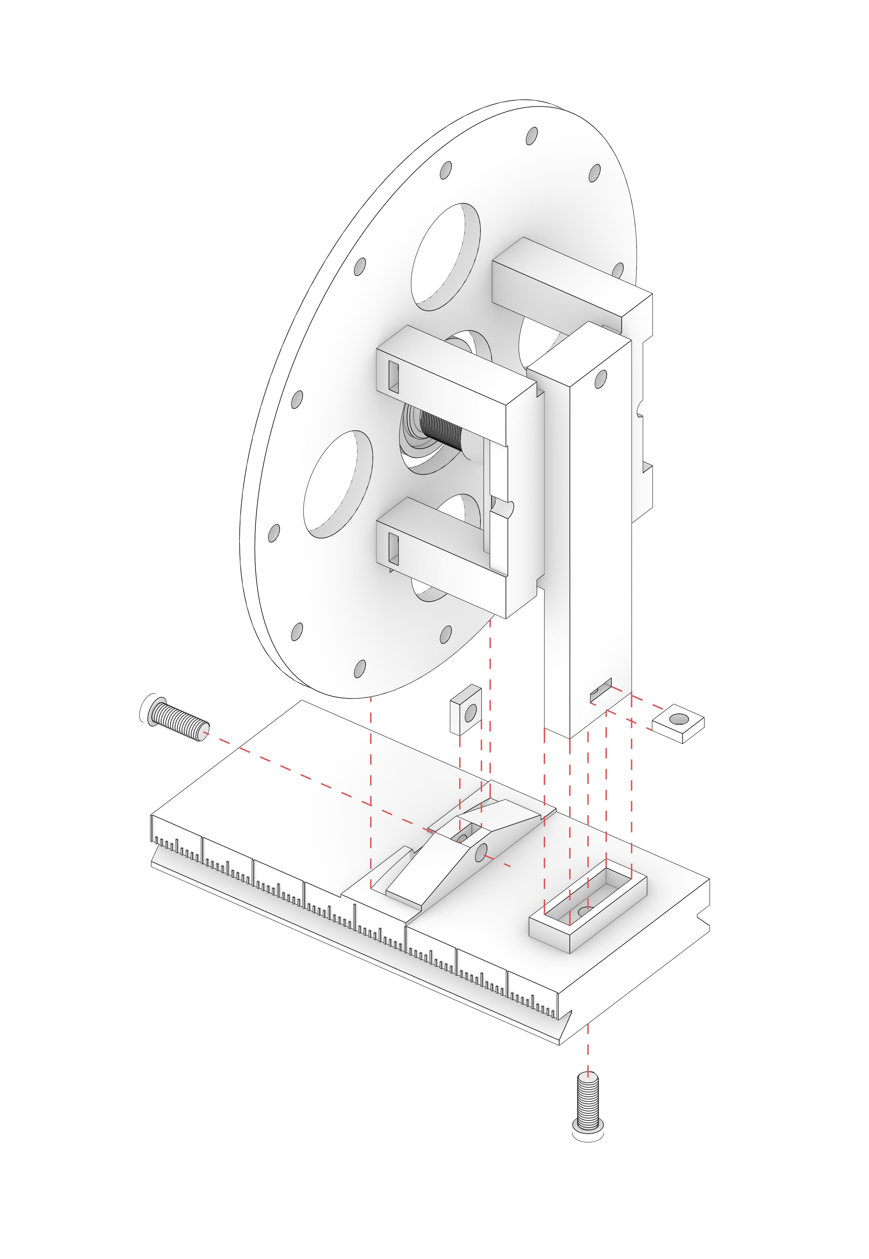
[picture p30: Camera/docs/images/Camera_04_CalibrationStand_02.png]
Screw the Ring and the attached Vertical Stand to the Slider
	- 
	- Put the bolt square nut in the cavity inside the Vertical stand and the Slider.
	- Use the bolts to secure everything in place.
4. **Attach the sensor:**
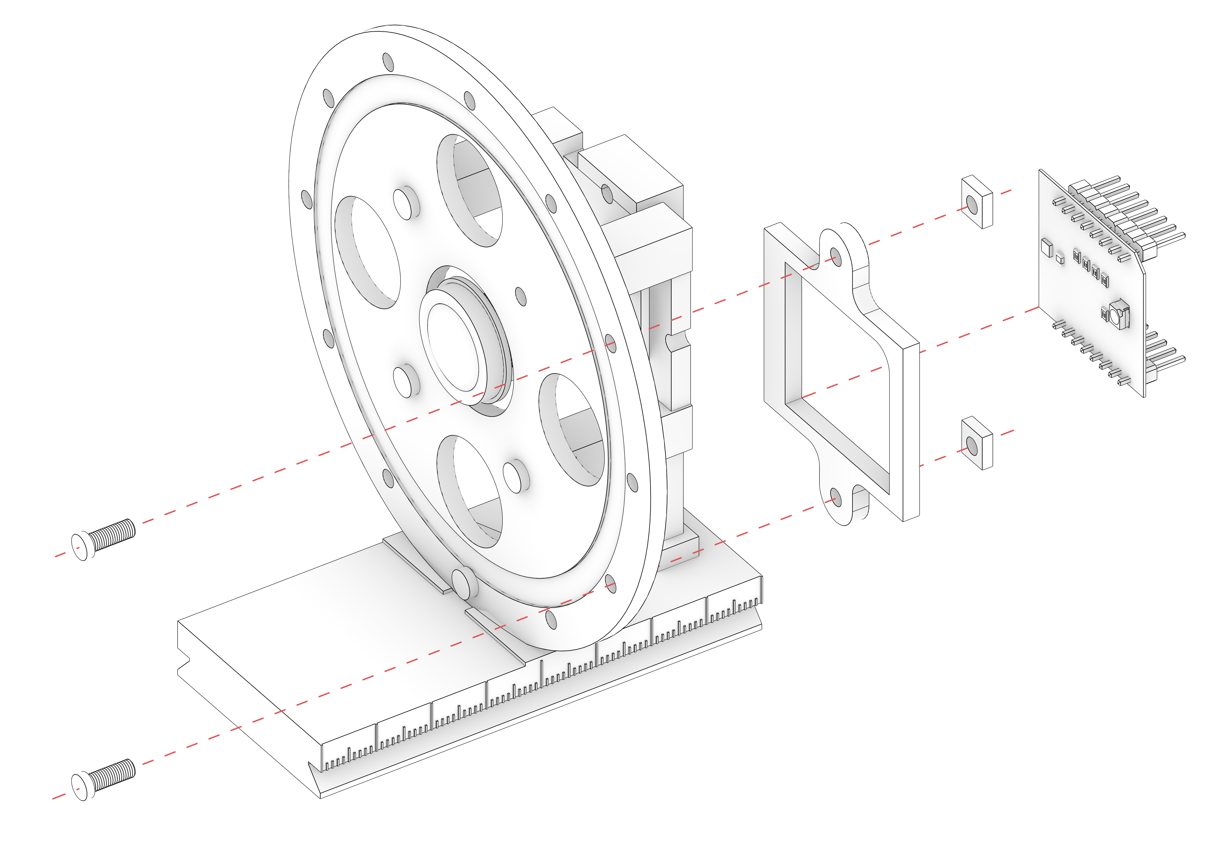
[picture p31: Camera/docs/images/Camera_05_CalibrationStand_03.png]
Screw the Sensor Bracket and attach the lux sensor
	- .
	- Attach the bracket for the _Ambient2Click_ lux Sensor to the Camera Ring. You can use any of the bolt holes on the edges, however it is convenient in your situation.
	- Put the Sensor itself in the bracket and secure it with a tape, or simply glue it with a hot glue gun.
	- Put a milky white tape on the hole in the Ring where the senor is facing out - it's to even out the light coming in.
	- The Sensor should be calibrated the same way as we did with other sensors for the Cube. Refer to [The Cube Guide](../../Cube/README.md).
5. **Mount on a rotating head:**
	- You can now mount it on a quick release rotating head or something similar, to be further used during calibration.
	- In our case, the true prallax point of the fisheye camera was at 1mm forward mark from the center of the Slider. So the Camera had to be slid 1mm backwards.

## End Result

It should look like this after the assembly:

Camera Calibration Stand Assembled Front
Camera Calibration Stand Assembled Back

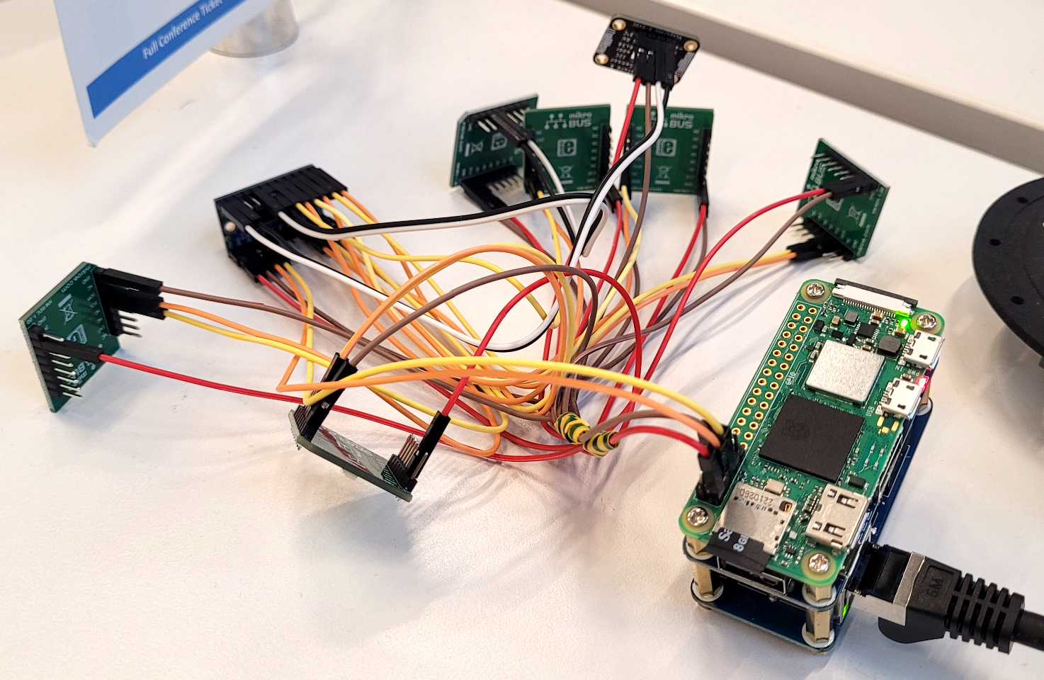
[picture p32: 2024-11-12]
Cube/docs/Images/Cube_Calibration_01.png

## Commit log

2024-11-05 First Test Commit
    [Materials_Bill.xlsx]
2024-11-07 Cube folder structure updates
    [Materials_Bill.xlsx]
2024-11-08 Cube Documentation updates
    [Calibration_Bench.dwg, Cube_Box_Enclosure.dwg]
2024-11-12 The Cube is done (almost)
    The Cube is done, only the nice final cube assembly animation is lacking...
2024-11-12 Camera repo updates
    Mainly adding hardware CAD files
    [Camera_Calibration_Slider.stl, Camera_Calibration_Slider.stp, Camera_Calibration_VerticalStand.stl, Camera_Calibration_VerticalStand.stp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]
2024-11-17 Camera repo updates
    Adding more files and documentation to the Camera repository.
    [Camera_Calibration_Slider.stl, Camera_Calibration_Slider.stp, Camera_Calibration_VerticalStand.stl, Camera_Calibration_VerticalStand.stp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]
2024-11-18 Camera repo updates
2024-11-18 Camera diagrams and updates
2024-11-19 Finalize Camera repo
2024-12-18 Camera Vignetting Correction
2025-01-09 Avoid double captures
    Removed routine that created two images at every exposure step to ensure the correct settings were received by picamera2. Replaced by start/stop camera at every step.
